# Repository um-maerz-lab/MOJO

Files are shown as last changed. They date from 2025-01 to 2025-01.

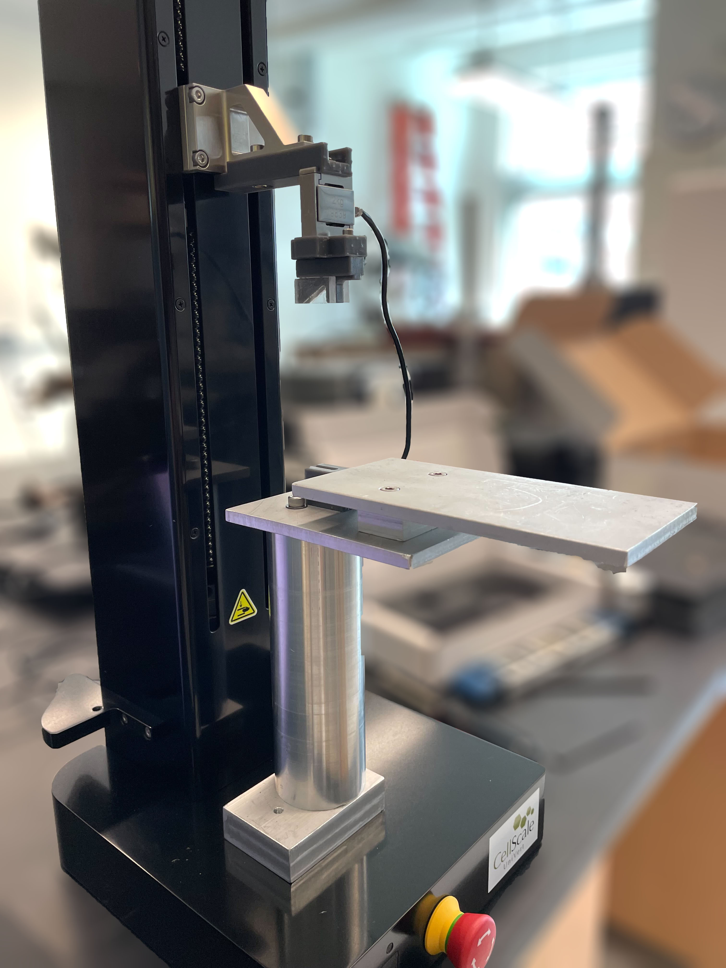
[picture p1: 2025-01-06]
Photos and Renders/MOJO Photo Isoview.jpg

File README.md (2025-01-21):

# Mobile Joint Operator (MoJO)
v1.0 - Oct. 2023
Maerz Lab, Department of Orthopaedic Surgery, University of Michigan
Primary Contact: Mike Newton (nemichae@umich.edu)
--------------------------------------------------------------------

This package includes:

- .STEP files for all custom parts of the MoJO platform
- A folder of photos and renders of the platform for reference
- .DOCX explanation of the mouse ACL rupture model
- .TMT file containing the ACL rupture loading profile
   * Built on UniVert software ver 12.28 (CellScale, Inc.)

Notes:

This platform was built for compatibility with the CellScale UniVert S2 uniaxial testing 
system with a 20N load cell. As of 2023, it is crucially important to select the S2 performance 
upgrade because the base UniVert model cannot accelerate to the 10 mm/s velocity required for 
the rupture displacement.

The knee bump, paw fixture, and top/bottom load cell adapter pieces were 3D printed using a 
Formlabs Form 3B printer out of Tough 2000 resin. Fixture designs were exported as .STEP files 
from Autodesk Fusion, converted to .STL files, imported into PreForm software, and sent directly 
to the printer. We utilized default print settings and 0.100 mm layer thickness.

Connections between parts were achieved using M3 and M5 bolts, along with brass tapping inserts 
(McMaster Part #s: 93722A204E308 and 93722A212E309). These inserts were threaded into 3D printed parts.

Other 3D printing technologies, such as filament-based printers, could also be used to print these 
fixtures. In this case, we would recommend a strong and durable filament such as ABS or nylon be used.

In our implementation of this platform, all pieces of the animal bed were fabricated from stainless 
steel and connected using M5 bolts. These pieces could also be 3D printed, though slight changes to
hole diameters may need to be made to accomodate threaded inserts.

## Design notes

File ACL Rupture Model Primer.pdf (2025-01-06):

### ACL Rupture by Tibial Compression: A Primer Maerz Lab | University of Michigan | Feb. 2024

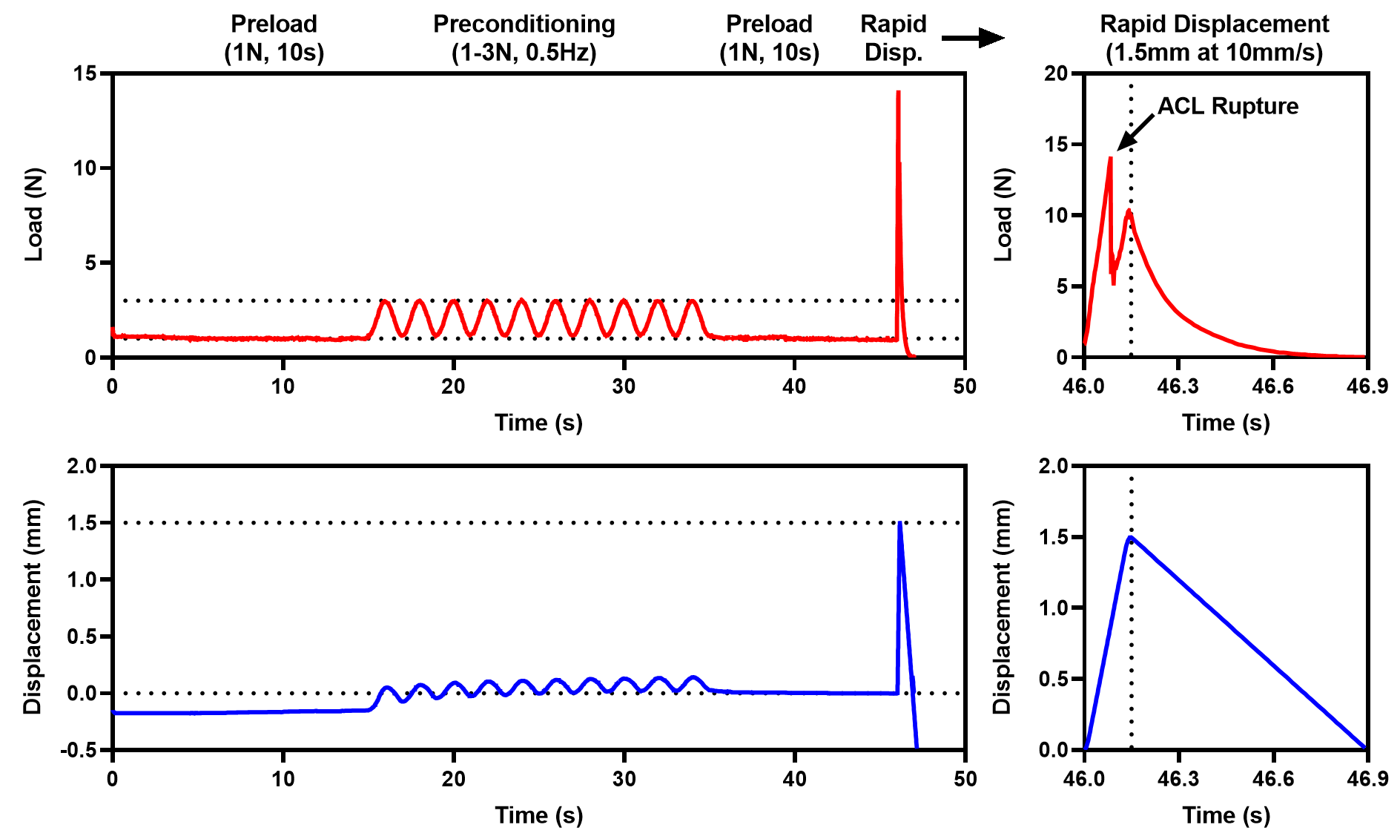
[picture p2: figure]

Figure 1. Full mouse ACL rupture mechanical protocol (left), rapid displacement and ACL rupture (right).

We utilize a model of non-invasive ACL rupture based on mechanical tibial compression, so named because the tibia is compressed while the ankle and knee are held in flexion, causing anterior tibial subluxation – see page 3 for a diagram. Tibial compression-induced ACL rupture was described in mice by Christiansen et al [1], and later adapted to rats by Maerz et al [2]. The mouse protocol consists of a preload, preconditioning cycles, another preload, and finally a rapid 1.5mm displacement, followed by immediate unloading. The preload and preconditioning cycles are discussed in more depth on page 2. Rapid compression causes the tibia to sublux anterior to the femur, stressing and eventually rupturing the ACL. Maerz et al [2] utilized motion capture in rats and demonstrated that the motion profile of this injury recapitulates the major proposed mechanism of clinical, sports-related ACL injury as described by Koga et al [3] (see page 4 for a figure demonstrating the mechanism). Rapid displacement is crucial, as slower displacements can result in physeal displacement or avulsion fracture [2], where the ACL fails at the ligament-bone interface rather than midsubstance and pulls a chunk of bone out with it – both of these represent fundamentally different joint injuries and are less consistent and not as broadly representative of clinical ACL rupture. It is theoretically possible to implement a mouse-specific displacement strain, relative to the ankle-to-knee length of each individual animal, but this is impractical and the 1.5mm displacement works with a high success rate in both sexes across a broad range of ages.

[1] Christiansen et al, Osetoarthrit Cartil 2012, doi: 10.1016/j.joca.2012.04.014
[2] Maerz et al, Ann Biomed Eng 2015, doi: 10.1007/s10439-015-1292-9
[3] Koga et al, Am J Sports Med 2010, doi: 10.1177/0363546510373570

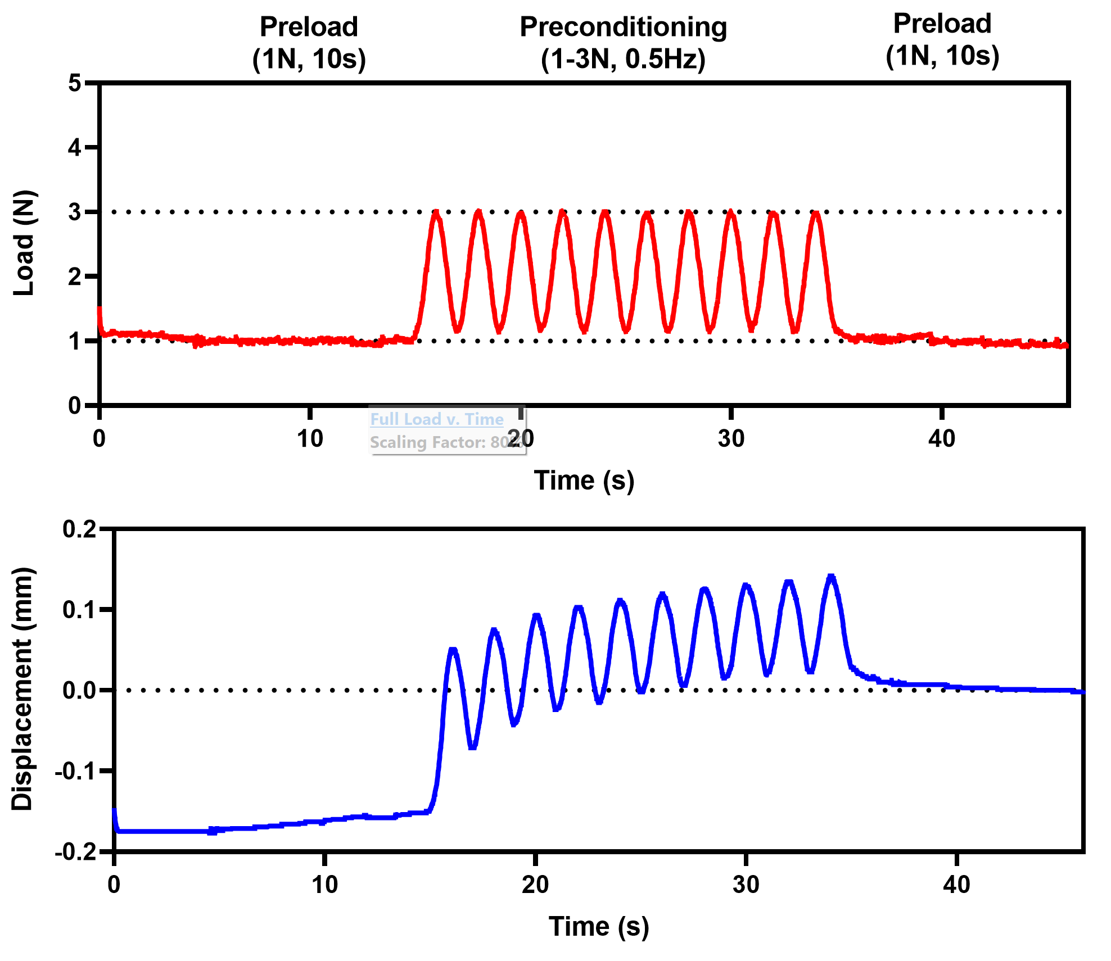
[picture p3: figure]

Figure 2. Preload and preconditioning cycles only.

Proper preconditioning of the ligament prior to the rapid displacement is important to ensure the ligament is fully elongated at the time of the displacement, increasing the chance of a successful, full thickness ACL rupture. Ligaments are viscoelastic tissues, meaning that the rate of loading affects the mechanical response of the ligament. A ligament loaded quickly will behave more stiffly than one loaded more slowly, and a ligament held at a steady load will undergo creep, ie. the ligament will gradually elongate when held at a consistent load. The reasons for this mechanical behavior are complex and not completely understood, but some combination of water egress and collagen fiber recruitment/alignment are understood to be involved. By applying preload and preconditioning cycles prior to rapid displacement, we can “warm up” or “condition” the ligament and attenuate the “viscous” portion of this response, such that the ligament behaves more elastically during the displacement – this can be observed by comparing displacement during the initial preload, where the ligament undergoes considerable creep, to that during the final preload, where an approximate steady-state displacement is reached by the end. We can observe that the joint ends up being more compressed at the end of preconditioning compared to the beginning (with the ligament therefore in tension, due to anterior tibial subluxation). Similarly, during cyclic preconditioning, the ligament can be seen to elongate with each cycle (ie. the displacement increases), however by the final cycles, the rate of this elongation slows and approaches an equilibrium. Preloading and preconditioning also help to increase fiber recruitment across the ligament, increasing the chances of a full thickness tear (as opposed to a partial tear).

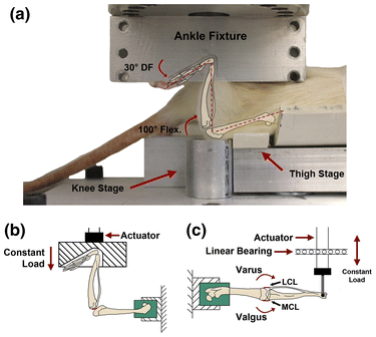
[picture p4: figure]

Figure 3. Tibial Compression Model of ACL Rupture. From Maerz et al [2].

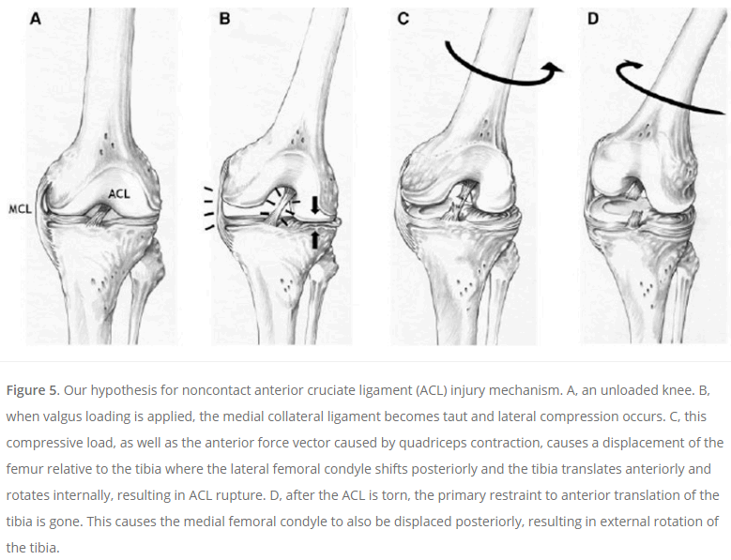
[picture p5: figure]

Figure 4. Mechanism for clinical, non-contact ACL injury. From Koga et al [3].

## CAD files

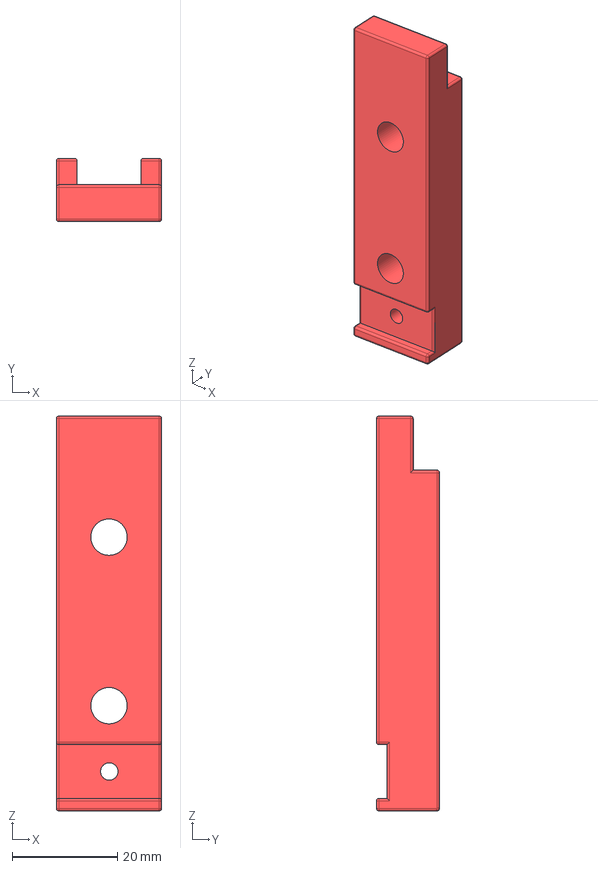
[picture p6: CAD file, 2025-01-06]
Fixture Designs and Print Files/MoJO STEP Files/top_actuator_to_loadcell_adapter.step
20.0 x 12.0 x 75.0 mm

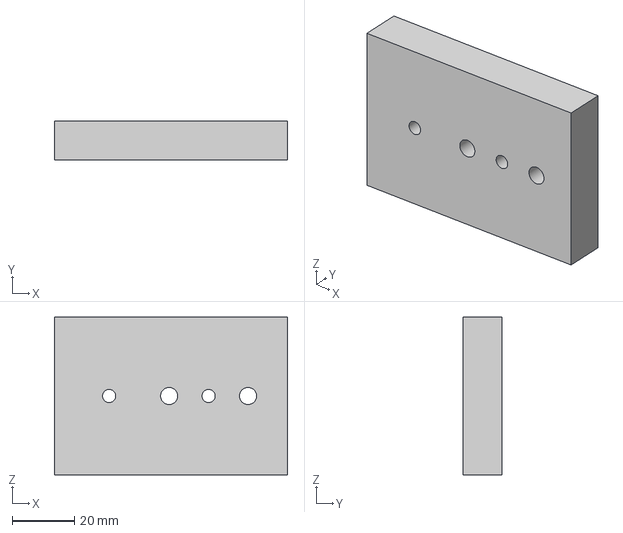
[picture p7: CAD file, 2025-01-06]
Fixture Designs and Print Files/MoJO STEP Files/animal_bed_baseplate_adapter.step
75.0 x 12.7 x 50.8 mm

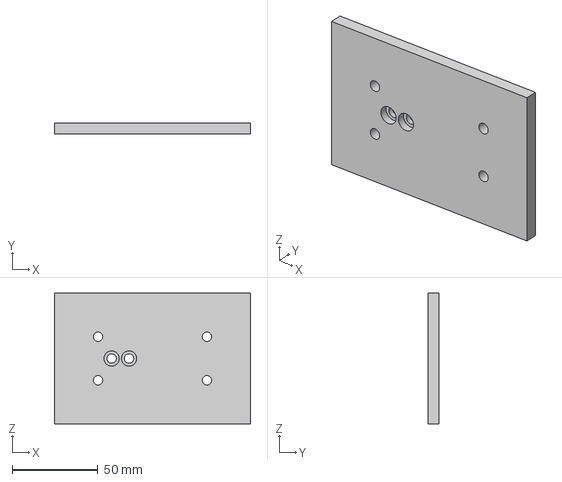
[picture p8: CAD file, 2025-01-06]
Fixture Designs and Print Files/MoJO STEP Files/animal_bed_lower_stage.step
114.3 x 6.35 x 76.2 mm

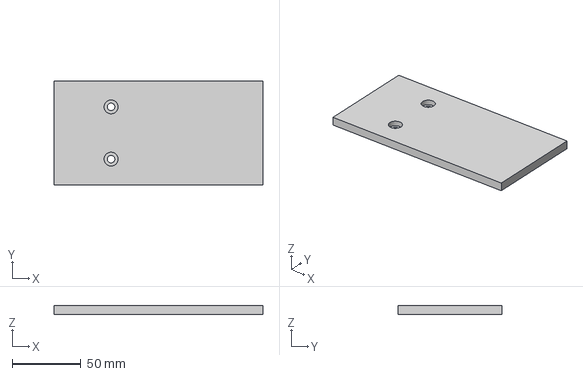
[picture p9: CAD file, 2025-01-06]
Fixture Designs and Print Files/MoJO STEP Files/animal_bed_upper_stage.step
152.4 x 76.2 x 6.35 mm

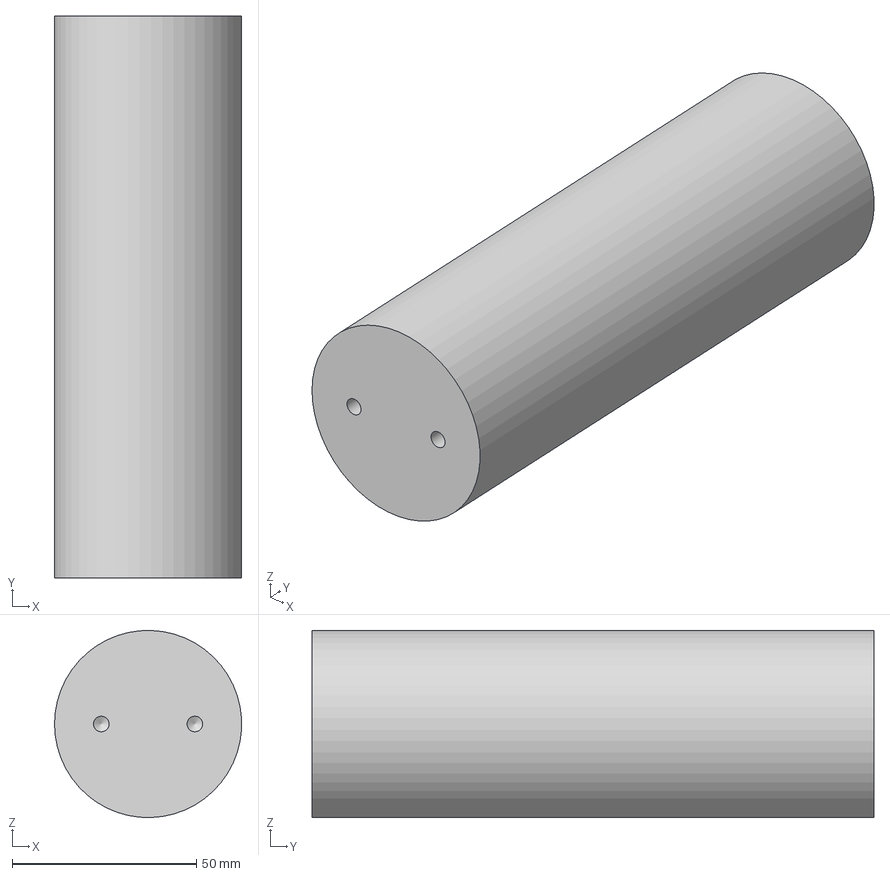
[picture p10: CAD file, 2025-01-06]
Fixture Designs and Print Files/MoJO STEP Files/animal_bed_cylinder.step
50.8 x 152.4 x 50.8 mm

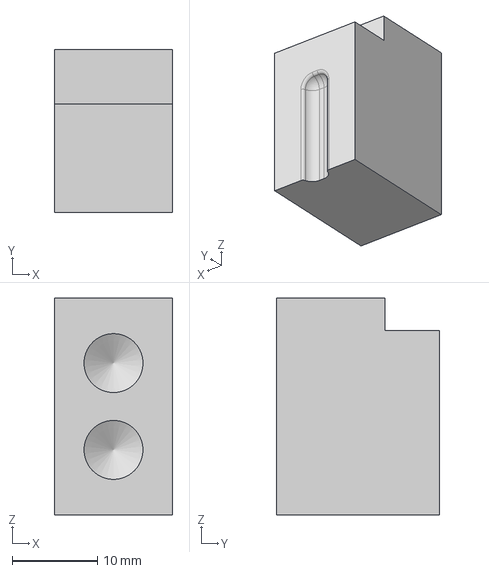
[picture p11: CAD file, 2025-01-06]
Fixture Designs and Print Files/MoJO STEP Files/mouse_knee_bump.step
13.8 x 19.1 x 25.4 mm

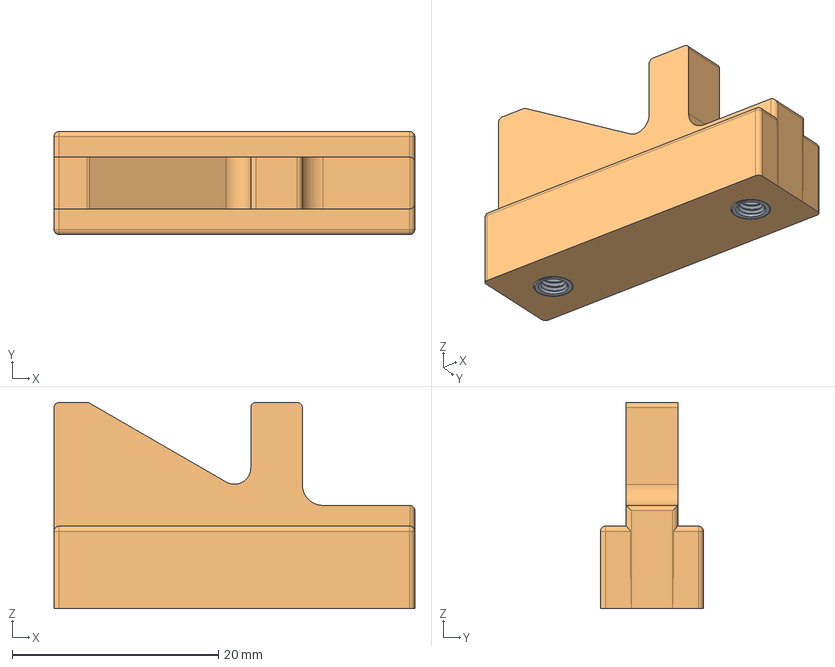
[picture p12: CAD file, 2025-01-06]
Fixture Designs and Print Files/MoJO STEP Files/mouse_paw_fixture.step
35.0 x 10.0 x 20.0 mm
mouse paw fixture v1 (1)
93722A204_M3 x 5.94mm Brass Tapping Inserts for Plastic x 2

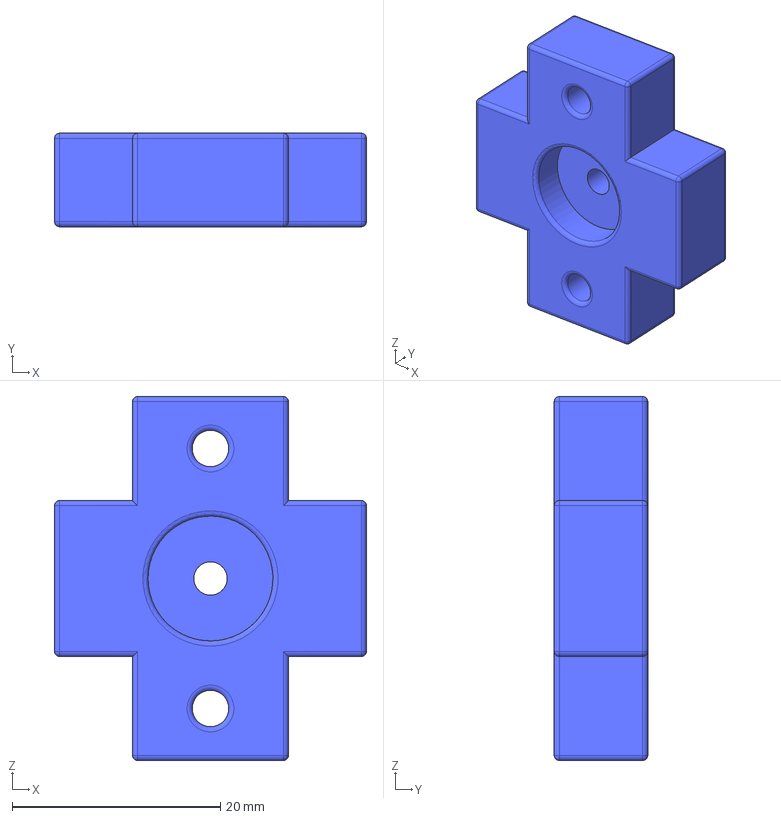
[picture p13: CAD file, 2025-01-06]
Fixture Designs and Print Files/MoJO STEP Files/bottom_loadcell_to_ankle_adapter.step
30.0 x 9.00 x 35.0 mm

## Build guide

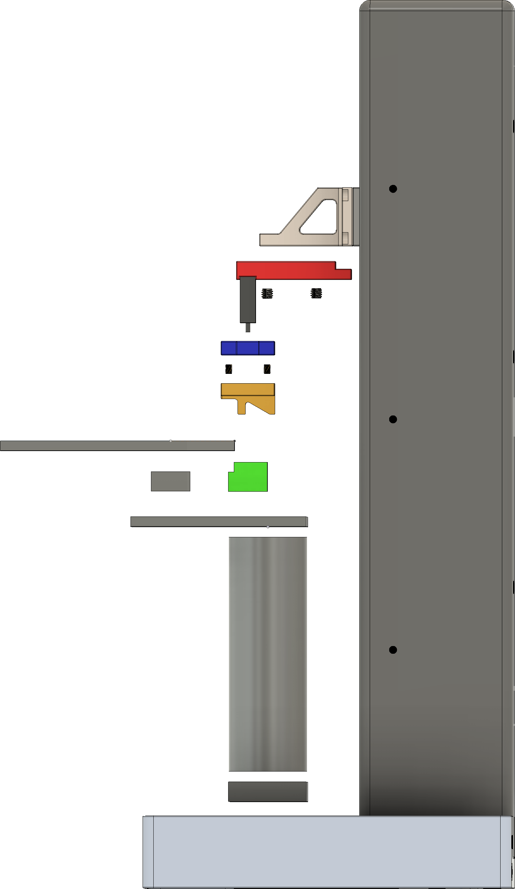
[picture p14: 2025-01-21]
Photos and Renders/MOJO Assembly Exploded Side.png

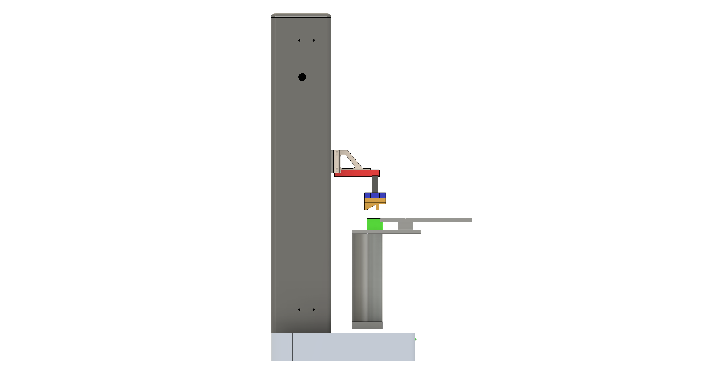
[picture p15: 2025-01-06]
Photos and Renders/MOJO Assembly Side.png
